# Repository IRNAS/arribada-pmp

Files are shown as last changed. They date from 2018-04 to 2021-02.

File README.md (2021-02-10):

# Arribada Penguin Monitoring Platform - v2 - development
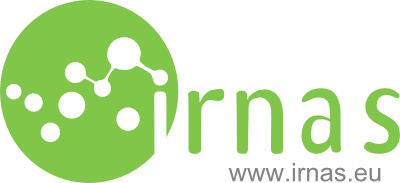
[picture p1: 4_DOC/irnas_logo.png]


Arribada Penguin Monitoring Platform (APMP) is a standalone device featuring a Raspberry Pi and a Raspberry Pi Camera Module with a number of additonal features. The below image is of previous version to form the list of necessary changes.



## Block diagram
Block diagram below shows the key features of Arribada PMP device. Device captures photos or video, measure temperature, humidity and air pressure, capture locations and charge batteries with solar cells. Penguin Monitoring Platform can communicates with LoRa and Rock Block or Lacuna.
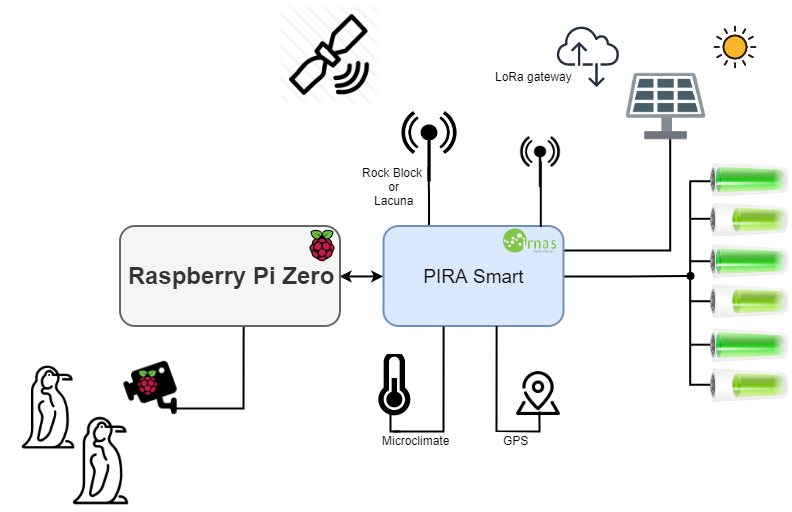
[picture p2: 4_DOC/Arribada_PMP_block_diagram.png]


## Key user features - v2
* Capture image/video at defined intervals
* Report system status/sensors via Lora (optional)
* Report system status/sensors via RockBlock Iridium (optional)
* Optional sensors:
  * Ultrasonic distance
  * Temperatures
  * GPS - location
* Power:
  * Batteries
  * Solar charging
* USB flash drive - user removable - contains all images and other captured data
  * contains images/videos
  * contains json with settings
* SD card with OS is read-only and not to be removed
* on/off switch
* 2x push button
  * button 1: test mode - push to turn on the system for 10 minutes
  * button 2: general purpose
* Test mode:
  * WiFi enabled, user can connect and check camera image or download all images
  * Each time test mode is enabled an image is taken.
* Bluetooth:
  * System status printout
  * Enable test mode
  * Configure settings
* Lora:
  * Enable test mode 
  * Configure settings
  * LacunaSpace communication
 
## Key user stories - v2
1. Penguin camera - Install on a pole in Antarctica. Arrive at location and turn on. Push button for test mode. See images via WiFi on smartphone or leave running and remove USB. To check camera alignment and correct operation. Leave device running for year or more, come pack and swap USB flash drive. Meanwhile real-time reporting via Lora or Lacuna, each day.
1. River camera - Install above a river with ultrasonic sensor and optional rockblock connection. Once above river enable the test mode via bluetooth. Check via WiFi the alignment and operation. Leave running and get real time sensor data. retrieve in a year to get back the photos.
1. TBD

## Configurable parameters - settings - v2
All the setings are defined as Environmental vairables in Linux, settings are changed using one of the following methods: json file present on the USB flash drive, system auto-updates values from it, via lora or via Balena if used

* User definable parameters:
 * capture schedule per month:
   * start time (UTC) - daily - fixed hour or `sunrise` (default 0:00)
   * end time (UTC) - daily - fixed hour or `sunset`(default 23:59)
   * interval (in minutes) - 0 to 24*60 (default 60)
 * location (automatic if GPS present):
   * lat (used for sunrise/sunset calculation)
   * lon (used for sunrise/sunset calculation)
 * capture type:
   * image
    * flash config
   * video
 * pira variables:
   * all timer values and defaults
   * lora parameters
   * rockblock parameters
   * sensor reporting interval
 * battery settings:
   * empty: default 10% - do not wake up the RPi below that
   * low-battery: default 30% - wake up only once a day
   * normal: general operation

## Specification

Device consists of:
 * Camera unit:
    * Raspberry Pi Zero W
    * Raspberry Pi Camera Module V2
    * Sandisk 16GB microSD card
    * Pira Smart V2 integrated board with battery mounts
    * 6x 18650 LiPo Cell 2900mAh/4.2V
    * Nanuk NANO 330 waterproof enclosure
    * I2C display for status
    * 2x user button
 * Optional:
    * Flash
    * Lora antenna
    * Rockblock Iridium or Lacuna module
    * Ultrasonic sensor
    * Thermometer
 * Solar power:
    * 2x Voltaic Systems 6V 6W solar panel
    * 2x Voltaic Systems solar panel extension cable
    * Multi-directional solar panel mount
 * Accessories
    * Allen-key tool for mounting
    * SD to microSD adapter
 * Mounting:
   * Simple strap mount (default)
   * Advanced KORUZA mount (optional)
 * Additionally required and not included
    * Pole (round or square) up to 50mm in diameter
    * Metric wrench size 13
    * Compass and tilt measuring device for pointing the solar panels
    
 ## Key desing considerations
 * Battery protection consider LC05111CMT for every 2 cells in parallel
 * Consider battery low temperature charge cutoor toprotect cells in winter

## License

All our projects are as usefully open-source as possible.

Hardware including documentation is licensed under [CERN OHL v.1.2. license](http://www.ohwr.org/licenses/cern-ohl/v1.2)

Firmware and software originating from the project is licensed under [GNU GENERAL PUBLIC LICENSE v3](http://www.gnu.org/licenses/gpl-3.0.en.html).

Open data generated by our projects is licensed under [CC0](https://creativecommons.org/publicdomain/zero/1.0/legalcode).

All our websites and additional documentation are licensed under [Creative Commons Attribution-ShareAlike 4 .0 Unported License](https://creativecommons.org/licenses/by-sa/4.0/legalcode).

What this means is that you can use hardware, firmware, software and documentation without paying a royalty and knowing that you'll be able to use your version forever. You are also free to make changes but if you share these changes then you have to do so on the same conditions that you enjoy.

Koruza, GoodEnoughCNC and IRNAS are all names and marks of Institut IRNAS Race. 
You may use these names and terms only to attribute the appropriate entity as required by the Open Licences referred to above. You may not use them in any other way and in particular you may not use them to imply endorsement or authorization of any hardware that you design, make or sell.

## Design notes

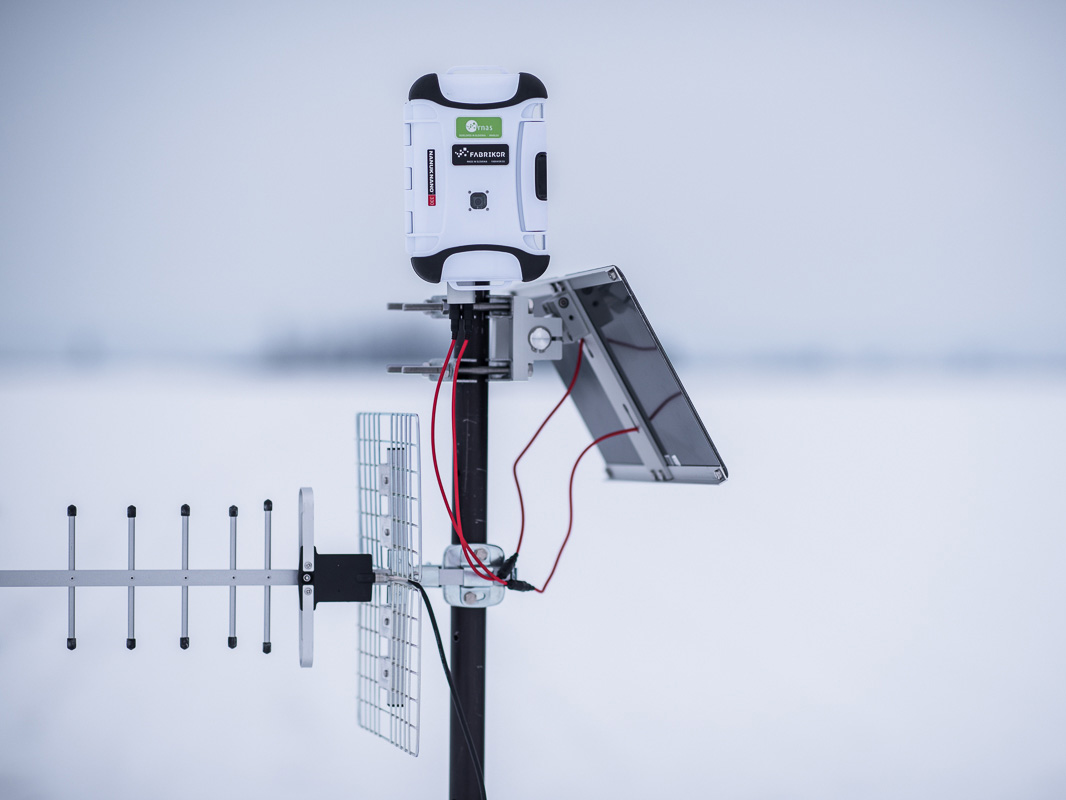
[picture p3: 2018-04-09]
pics/apmp-2.jpg

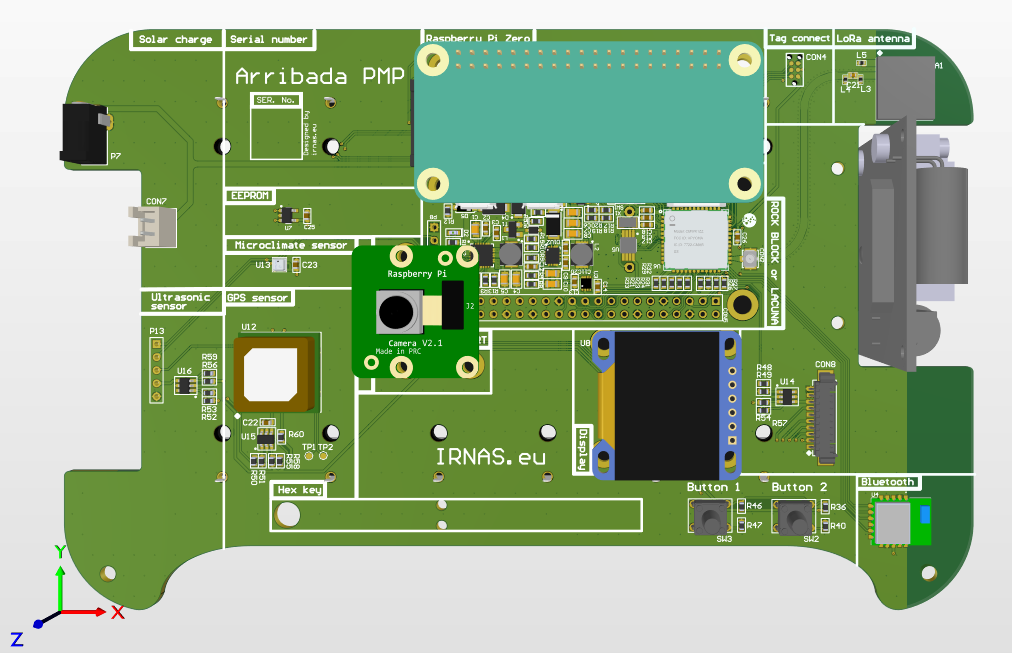
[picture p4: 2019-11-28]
6_RELEASE/V1.2/Arribada PMP_V1.2_SOURCE/04_OUTPUT_FILES/Pics/PMP_PCB_top.png

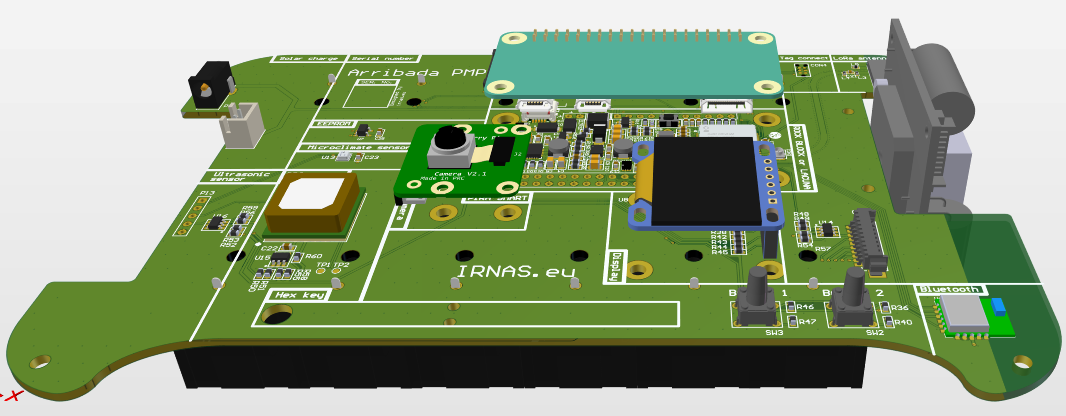
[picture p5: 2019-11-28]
6_RELEASE/V1.2/Arribada PMP_V1.2_SOURCE/04_OUTPUT_FILES/Pics/PMP_PCB_angle.png

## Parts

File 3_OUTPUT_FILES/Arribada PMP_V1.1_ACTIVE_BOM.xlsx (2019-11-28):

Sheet: Part List Report
 | Component list |  |  | Arribada PMP
 | Source Data From: | Arribada PMP_V0.1_ACTIVE_BOM.BomDoc |  |  | Contact:
 | Project: | Arribada-PMP.PrjPCB
 | Variant: | None |  |  |  |  |  |  | IRNAS
 | Report Date: | 30. 09. 2019 | 10:43 |  |  |  |  |  | www.irnas.eu
 | Print Date: | 2019-09-30 | 43738.447
# | Manufacturer Part Number 1 | Manufacturer 1 | Description | Footprint | Category | Quantity | Supplier 1 | Supplier Part Number 1 | Supplier Order Qty 1 | Supplier Stock 1 | Supplier Unit Price 1 | Supplier Subtotal 1 | Supplier Currency 1
1 |  |  |  | OLED SSD1306 |  | 1 |  | OLED SSD 1306 display
2 | C0603C106M8PACTU | KEMET | 10uf/0603/20% | CAP0603 |  | 2 | Farnell | 2820985 | 10 | 4806 | 0.32 | 3.19 | GBP
3 | SR42I010-R | Antenova | Antenna SMD -4dBi Gain 870MHz/928MHz Automotive 7-Pin SMD T/R | LORA_PCB_ANTENNA |  | 1 | Mouser | 237-SR42I010-R | 1 | 1418 | 2.36 | 2.36 | USD
4 |  |  | BATERRY HOLDER 18650 | BATTERY HOLDER 18650 |  | 6 |  | Battery holder for 18650
5 | CR-2032/VCN | Panasonic BSG | BATT LITH COIN 3V CELL PC PINS | CR-2032/VCN |  | 1 | Farnell | 1892670 | 1 | 1798 | 0.94 | 0.94 | GBP
6 |  |  | BATTERY PROTECTION | BATTERY PROTECTION |  | 3 |  | Battery protection
7 | CR0603-J/-000ELF | Bourns | BOURNS - CR0603-J/-000ELF - RES, THICK FILM, 0R, 5%, 0.1W, 0603 | RES0603 |  | 9 | Farnell | 2008343 | 10 | 35503 | 0.01 | 0.12 | GBP
8 | CR0603-J/-000ELF | Bourns | BOURNS - CR0603-J/-000ELF - RES, THICK FILM, 0R, 5%, 0.1W, 0603 | RES0603 |  | 10 | Farnell | 2008343 | 10 | 35503 | 0.01 | 0.12 | GBP
9 | HSMS-C190 | Broadcom | BROADCOM LIMITED - HSMS-C190 - LED, RED, 10MCD, 626NM | LED0603 |  | 1 | Farnell | 2497356
10 | U.FL-R-SMT-1(10) | Hirose | CONN UMC JACK STR 50 OHM SMD | ufl connector smd | Connectors, Interconnects | 1 | Farnell | 1688077
11 | LFXTAL009678 | IQD | CRYSTAL, 32.768KHZ, 12.5PF, SMD | LFXTAL009678 |  | 1 | Farnell | 2449398 | 5 | 4216 | 0.39 | 1.95 | GBP
12 | BZT52C6V2 | Diodes Zetex | DIODES INC. - BZT52C6V2 - DIODE, ZENER, 6.2V, 0.5W, SOD-123 | SOD123 |  | 1 | Farnell | 1902438 | 5 | 12142 | 0.12 | 0.62 | GBP
13 | DMG6602SVT | Diodes | DIODES INC. - DMG6602SVT - MOSFET, NP CH, , 30V, 3.4, ATSOT23 | TSOT26 |  | 1 | Farnell | 2061522 | 5 | 36143 | 0.29 | 1.48 | GBP
14 | DMG6602SVT | Diodes | Dual MOSFET, N and P Channel, 3.4 A, 30 V, 0.038 ohm, 10 V, 1 V | TSOT26 |  | 3 | Farnell | 2061522 | 5 | 36143 | 0.29 | 1.48 | GBP
15 |  |  | Header, 4-Pin | HDR1X4 |  | 2 |  | Header 2.54 mm, Header 2.54mm
16 |  |  | Header, 5-Pin | HDR1X5 |  | 1 |  | Header 2.54 mm
17 |  |  | Header, 11-Pin | HDR1X11 |  | 1 |  | Header 2.54mm
18 |  |  | Header, 20-Pin, Dual row | HDR2X20 |  | 2 |  | [NoParam], RPi header
19 | HSME-C191 | Broadcom Avago | HSME-C191 - LED, Green, SMD, 0603, 20 mA, 2.1 V, 572 nm | LED0603 |  | 1 | Farnell | 1219743 | 5 | 16346 | 0.31 | 1.53 | GBP
20 | BME280 | Bosch Tools | Humidity Temperature Sensor 0 ~ 100% RH I²C, SPI ±3% 1s Surface Mount | BME280 |  | 1 | Digi-Key | 828-1063-6-ND | 1 | 58503 | 6.55 | 6.55 | USD
21 | BQ24296RGET | Texas Instruments | IC LI+ CHARGER PWR MGMT 24VQFN | QFN4x4 | Integrated Circuits (ICs) | 1 | Farnell | 2373541
22 | MCP1810T-30I/J8A | Microchip | IC REG LINEAR 3V 150MA 8VDFN | VDFN_2x2 |  | 1 | Farnell | 2678433 | 1 | 1222 | 0.39 | 0.39 | GBP
23 | ISL1208IU8Z-T7A | Renesas | IC RTC/CALENDAR I2C LP 8MSOP | TSOP65P500X110-8N |  | 1 | Farnell | 2543322
24 | MCFT000028 | Multicomp | Inductor RF Chip Multi-Layer 4.3nH 0.3nH 100MHz 8Q-Factor Air 300mA 210mOhm DCR 0402 Paper T/R | IND0402 |  | 2 | Farnell | 1711735 | 10 | 13389 | 0.02 | 0.17 | GBP
25 | LQP02TQ4N2B02D | Murata | Inductor RF Chip Multi-Layer 4.3nH 0.3nH 100MHz 8Q-Factor Air 300mA 210mOhm DCR 0402 Paper T/R | IND0402 |  | 1 | Farnell | 2871406 | 10 | 19898 | 0.12 | 1.21 | GBP
26 | MINISMDC150F/24-2 | Littelfuse | LITTELFUSE - MINISMDC150F/24-2 - POLYSWITCH, SMD, 1812, 1.5A | Chip2PinSM127P600-8N |  | 1 | Farnell | 1345929
27 | CMWX1ZZABZ-091 | Murata | Lora Module Murata | Lora Module ES0 |  | 1 | Farnell | 2802546 | 1 | 105 | 15.15 | 15.15 | GBP
28 | 24AA02E48T-I/OT | Microchip | MICROCHIP 24AA02E48T-I/OT EEPROM, EUI-48 Node Identity, 2 Kbit, 2 BLK (128K x 8bit), 400 kHz, I2C, SOT-23, 5 Pins | SOT95P280X145-5N |  | 1 | Farnell | 1688855 | 1 | 16808 | 0.18 | 0.18 | GBP
29 | RN4871-V/RM118 | Microchip | MICROCHIP RN4871-V/RM118 BLE MOD W/ANTENNA, 2.442MHZ, 0.1DBI New | RN4871 |  | 1 | Farnell | 2664514 | 1 | 2422 | 5.71 | 5.71 | GBP
30 | MCWR06X1000FTL | Multicomp | MULTICOMP - MC0063W06031100R - RES, THICK FILM, 100R, 1%, 0.063W, 0603 | RES0603 |  | 2 | Farnell | 2447227 | 10 | 462054 | 0.01 | 0.06 | EUR
31 | MC0.063W06031%100R | Multicomp | MULTICOMP - MC0063W06031100R - RES, THICK FILM, 100R, 1%, 0.063W, 0603 | RES0603 |  | 9 | Farnell | 9330364
32 | MC0603B473K500CT | Multicomp | MULTICOMP - MC0603B473K500CT - CAP, MLCC, X7R, 47NF, 50V, 0603 | CAP0603 |  | 1 | Farnell | 1759116 | 10 | 36181 | 0.02 | 0.22 | GBP
33 | MC0805X226M6R3CT | Multicomp | MULTICOMP - MC0805X226M6R3CT - CAP, MLCC, X5R, 22UF, 0805 | CAP0805 |  | 4 | Farnell | 1759415
34 | MCMR06X102JTL | Multicomp | MULTICOMP - MCMR06X102 JTL - RES, CERAMIC, 1K, 5%, 0.1W, 0603 | RES0603 |  | 2 | Farnell | 2073354 | 10 | 150 | 0.01 | 0.07 | GBP
35 | MCMR06X103JTL | Multicomp | MULTICOMP - MCMR06X103 JTL - RES, CERAMIC, 10K, 5%, 0.1W, 0603 | RES0603 |  | 3 | Farnell | 2073356 | 10 | 8524 | 0.01 | 0.08 | GBP
36 | MCMR06X103JTL | Multicomp | MULTICOMP - MCMR06X103 JTL - RES, CERAMIC, 10K, 5%, 0.1W, 0603 | RES0603 |  | 3 | Farnell | 2073356 | 10 | 8524 | 0.01 | 0.08 | GBP
37 | MCMR06X104JTL | Multicomp | MULTICOMP - MCMR06X104 JTL - RES, CERAMIC, 100K, 5%, 0.1W, 0603 | RES0603 |  | 4 | Farnell | 2073357 | 10 | 19720 | 0.01 | 0.07 | GBP
38 | MCMR06X104JTL | Multicomp | MULTICOMP - MCMR06X104 JTL - RES, CERAMIC, 100K, 5%, 0.1W, 0603 | RES0603 |  | 6 | Farnell | 2073357 | 10 | 19720 | 0.01 | 0.07 | GBP
39 | MCMR06X471JTL | Multicomp | MULTICOMP - MCMR06X471 JTL - RES, CERAMIC, 470R, 5%, 0.1W, 0603 | RES0603 |  | 2 | Farnell | 2073513 | 10 | 7623 | 0.01 | 0.05 | GBP
40 | MCMR06X2201FTL | Multicomp | MULTICOMP - MCMR06X2201FTL - RES, CERAMIC, 2K2, 1%, 0.1W, 0603 | RES0603 |  | 1 | Farnell | 2073429 | 10 | 25875 | 0.01 | 0.10 | GBP
41 | MCMR06X4701FTL | Multicomp | MULTICOMP - MCMR06X4701FTL - RES, CERAMIC, 4K7, 1%, 0.1W, 0603 | RES0603 |  | 2 | Farnell | 2073509 | 10 | 27235 | 0.01 | 0.10 | GBP
42 | MCMR06X5601FTL | Multicomp | MULTICOMP - MCMR06X5601FTL - RES, CERAMIC, 5K6, 1%, 0.1W, 0603 | RES0603 |  | 1 | Farnell | 2073537 | 10 | 960 | 0.01 | 0.10 | GBP
43 | MCWR06X1503FTL | Multicomp | MULTICOMP - MCWR06X1503FTL - RES, THICK FILM, 150KOHM, 1%, 0.1W | RES0603 |  | 1 | Farnell | 2447254 | 10 | 63490 | 0.01 | 0.05 | GBP
44 | MCWR06X2200FTL | Multicomp | MULTICOMP - MCWR06X2200FTL - RES, THICK FILM, 220R, 1%, 0.1W, 0603 | RES0603 |  | 1 | Farnell | 2447298 | 10 | 268348 | 0.01 | 0.06 | EUR
45 | MCWR06X3302FTL | Multicomp | MULTICOMP - MCWR06X3302FTL - RES, THICK FILM, 33K, 1%, 0.1W, 0603 | RES0603 |  | 1 | Farnell | 2447342 | 10 | 85218 | 0.01 | 0.05 | GBP
46 | MCWR06X3901FTL | Multicomp | MULTICOMP - MCWR06X3901FTL - RES, THICK FILM, 3K9, 1%, 0.1W, 0603 | RES0603 |  | 1 | Farnell | 2447363 | 10 | 27101 | 0.01 | 0.05 | GBP
47 | C0402C229C5GACTU | KEMET | Multilayer Ceramic Capacitors MLCC - SMD/SMT 50volts 1.8pF C0G | CAP0402 |  | 1 | Farnell | 1800795 | 10 | 31735 | 0.05 | 0.53 | GBP
48 | GRM188R61C106KAALD | Murata | Multilayer Ceramic Capacitors MLCC - SMD/SMT 0603 10uF 16volts X5R 10% | CAP0603 |  | 2 | Farnell | 2611923 | 10 | 94340 | 0.26 | 2.61 | GBP
49 | FDSD0420-H-1R5M=P3 | Murata | MURATA - FDSD0420-H-1R5M=P3 - INDUCTOR, SHIELDED, 1.5UH, 5.1A, 20% | FDSD0402 |  | 2 | Farnell | 2530091 | 5 | 15 | 0.83 | 4.17 | GBP
50 | GRM188R61C475KAAJD | Murata | MURATA - GRM188R61C475KAAJD - CAP, MLCC, X5R, 4.7UF, 16V, 0603 | CAP0603 |  | 1 | Farnell | 2611924 | 10 | 81661 | 0.24 | 2.39 | GBP
51 | GRM188R61C475KAAJD | Murata | MURATA - GRM188R61C475KAAJD - CAP, MLCC, X5R, 4.7UF, 16V, 0603 | CAP0603 |  | 1 | Farnell | 2611924 | 10 | 81661 | 0.24 | 2.39 | GBP
52 | GRM188R61H105KAALD | Murata | MURATA - GRM188R61H105KAALD - CAP, MLCC, X5R, 1UF, 50V, 0603 | CAP0603 |  | 2 | Farnell | 1845736
53 | GRM188R61H105KAALD | Murata | MURATA - GRM188R61H105KAALD - CAP, MLCC, X5R, 1UF, 50V, 0603 | CAP0603 |  | 1 | Farnell | 1845736
54 | GRM188R71C104KA01J | Murata | MURATA - GRM188R71C104KA01J - CAP, MLCC, X7R, 0.1UF, 16V, 0603 | CAP0603 |  | 4 | Farnell | 2688519
55 | GRM188R71C104KA01J | Murata | MURATA - GRM188R71C104KA01J - CAP, MLCC, X7R, 0.1UF, 16V, 0603 | CAP0603 |  | 2 | Farnell | 2688519
56 | MM3Z3V0T1G | ON Semiconductor | ON SEMICONDUCTOR - MM3Z3V0T1G - ZENER DIODE, 200MW, 3V, SOD-323 | SOD-323 2L |  | 1 | Farnell | 2463510 | 5 | 21905 | 0.12 | 0.61 | GBP
57 | MMBT3904 | NXP Semiconductors | ON SEMICONDUCTOR/FAIRCHILD - MMBT3904 - TRANSISTOR, NPN, SOT-23 | SOT23127P600-8N |  | 1 | Farnell | 9846727 | 5 | 72000 | 0.14 | 0.68 | GBP
58 |  |  | PCB top overlay Serial number frame | SERIAL NUMBER |  | 1
59 | 694102303002 | Wurth Electronics | Power Barrel Connector Jack 1.05mm ID (0.041"), 3.50mm OD (0.138") Through Hole, Right Angle | 732-5922-ND |  | 1 | Farnell | 2472141 | 10 | 183 | 0.63 | 6.30 | GBP
60 | SAM-M8Q-0 | u-blox | SAM-M8 RF Receiver BeiDou, Galileo, GLONASS, GNSS, GPS -160dBm | SAM-M8Q |  | 1 | Digi-Key | 672-1054-1-ND | 1 | 4378 | 25.00 | 25.00 | USD
61 | 1PS76SB10,115 | Nexperia | Small Signal Schottky Diode, Single, 30 V, 200 mA, 320 mV, 800 mA, 125 °C | SOD-323 |  | 2 | Farnell | 1081179 | 5 | 124792 | 0.17 | 0.85 | GBP
62 | MC0603X225K6R3CT | Multicomp | SMD Multilayer Ceramic Capacitor, 2.2 µF, 6.3 V, 0603 [1608 Metric], ± 10%, X5R, MC Series | CAP0603 |  | 1 | Farnell | 1759392 | 10 | 15721 | 0.06 | 0.55 | GBP
63 |  |  | SWITCH TACTILE SPST-NO 0.05A 32V | Tactile button |  | 1 | C&K Components | 2845727
64 | B3F-1070 | Omron | Tactile Switch, B3F Series, Top Actuated, Through Hole, Round Button, 100 gf, 50mA at 24VDC | BTN B3F-1070 |  | 2 | Farnell | 959698 | 5 | 3258 | 0.25 | 1.26 | GBP
65 | MC0805X106K160CT | Multicomp | TDK - CGA4J1X5R1C106K125AC - CAP, MLCC, X5R, 10UF, 16V, 0805 | CAP0805 |  | 4 | Farnell | 2320856
66 |  |  | TEST POINT ROUND SMD | TestPoint:1.2x1.2mm |  | 2
67 | TPS630701RNMT | Texas Instruments | TEXAS INSTRUMENTS - TPS630701RNMT - DC/DC CONV, BUCK-BOOST, 2.4MHZ, VQFN-15 | VQFN TPS |  | 1 | Farnell | 2643432
68 | B57321V2103J060 | TDK EPCOS | Thermistor, NTC, 10 kohm, B57321V2 Series, 4000 K, SMD, 0603 [1608 Metric] | RES0603 |  | 1 | Farnell | 1299914 | 10 | 24794 | 0.19 | 1.87 | GBP
69 | CRCW0603226KFKEA | Vishay | Thick Film Resistors - SMD 1/10watt 226Kohms 1% | RES0603 |  | 1 | Farnell | 2138531
70 | RCA060310R0FKEA | Vishay Dale | VISHAY - RCA060310R0FKEA - RES, AUTO, THICK FILM, 10R, 1%, 0603 | RES0603 |  | 1 | Farnell | 2616585 | 10 | 6813 | 0.01 | 0.12 | GBP
71 | RS1J-E3/61T | Vishay Semiconductors | VISHAY - RS1J-E3/61T.. - DIODE, FAST, 1A, 600V, SMD | SMC/DO-214AC |  | 1 | Farnell | 9550143 | 5 | 4450 | 0.25 | 1.24 | GBP
72 | SE30AFG-M3/6A | Vishay Semiconductors | VISHAY - SE30AFG-M3/6A - RECTIFIER, ESD, 400V, 3A, DO-221AC | SODFL127P600-8N |  | 2 | Farnell | 2313878 | 5 | 22049 | 0.31 | 1.57 | GBP
73 | 53261-1071 | Molex | Wire-To-Board Connector, Right Angle, 1.25 mm, 10 Contacts, Header, PicoBlade 53261 Series | PICOBLADE 10PIN |  | 1 | Farnell | 1125377 | 1 | 4313 | 0.86 | 0.86 | GBP
74 | B2B-XH-A(LF)(SN) | JST | Wire-To-Board Connector, Vertical, 2.5 mm, 2 Contacts, Header, XH Series, Through Hole, 1 Rows | JST_2PIN_TH |  | 1 | Farnell | 1516276 | 100 | 185326 | 0.06 | 6.06 | GBP
 |  |  |  |  |  | 145 |  |  | 449 |  |  | 103.444
Approved |  |  |  | Notes
 |  |  |  | pcs: |  | 1 |  | Total |  | 103.444 |  | USD
 |  |  |  |  |  |  |  | Price for 1pcs |  | 103.44 |  | USD

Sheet: Project Information
Project Full Path | D:\OneDrive\IRNAS-Common\_NEW-IRNAS-COMMON\Arribada-PMP\Electronics\Arribada-PMP.PrjPCB
Project Filename | Arribada-PMP.PrjPCB
Variant Name | None
Data-Source Filename | Arribada PMP_V0.1_ACTIVE_BOM.BomDoc
Data-Source Full Path | D:\OneDrive\IRNAS-Common\_NEW-IRNAS-COMMON\Arribada-PMP\Electronics\04_OUTPUT_FILES\Arribada PMP_V0.1_ACTIVE_BOM.BomDoc
Title | ACTIVE_BOM for BOM Document [Arribada PMP_V0.1_ACTIVE_BOM.BomDoc]
Total Quantity | 145
Report Time | 10:43
Report Date | 30. 09. 2019
Report Date & Tine | 30. 09. 2019 10:43
Output Name | ACTIVE_BOM
Output Type | BOM_PartType
Output Generator Name | BOM
Output Generator Description | Bill of Materials

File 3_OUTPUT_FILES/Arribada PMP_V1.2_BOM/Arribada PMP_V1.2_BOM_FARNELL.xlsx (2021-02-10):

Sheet: Altium Output
Supplier Part Number 1 | Quantity | Description | Designator | Supplier 1 | IRNAS Part No. | No PCB | Projekt | Farnell
237-SR42I010-R | 1 | Antenna SMD -4dBi Gain 870MHz/928MHz Automotive 7-Pin SMD T/R | A1 | Mouser |  | 5 |  | 237-SR42I010-R, 5,
2320856 | 4 | TDK - CGA4J1X5R1C106K125AC - CAP, MLCC, X5R, 10UF, 16V, 0805 | C1, C4, C5, C6 | Farnell |  | 5 |  | 2320856, 20,
2611924 | 2 | MURATA - GRM188R61C475KAAJD - CAP, MLCC, X5R, 4.7UF, 16V, 0603 | C2, C13 | Farnell | [NoParam], I-200001 | 5 |  | 2611924, 10,
1759116 | 1 | MULTICOMP - MC0603B473K500CT - CAP, MLCC, X7R, 47NF, 50V, 0603 | C3 | Farnell |  | 5 |  | 1759116, 5,
1759415 | 4 | MULTICOMP - MC0805X226M6R3CT - CAP, MLCC, X5R, 22UF, 0805 | C7, C8, C9, C10 | Farnell |  | 5 |  | 1759415, 20,
2611923 | 2 | Multilayer Ceramic Capacitors MLCC - SMD/SMT 0603 10uF 16volts X5R 10% | C11, C20 | Farnell |  | 5 |  | 2611923, 10,
2688519 | 7 | MURATA - GRM188R71C104KA01J - CAP, MLCC, X7R, 0.1UF, 16V, 0603 | C12, C15, C18, C22, C23, C25, C28 | Farnell | [NoParam], I-200005 | 5 |  | 2688519, 35,
1759392 | 1 | SMD Multilayer Ceramic Capacitor, 2.2 µF, 6.3 V, 0603 [1608 Metric], ± 10%, X5R, MC Series | C14 | Farnell |  | 5 |  | 1759392, 5,
1845736 | 6 | MURATA - GRM188R61H105KAALD - CAP, MLCC, X5R, 1UF, 50V, 0603 | C16, C17, C24, C26, C27, C29 | Farnell | I-200006, [NoParam] | 5 |  | 1845736, 30,
2820985 | 1 | 10uf/0603/20% | C19 | Farnell |  | 5 |  | 2820985, 5,
2627398 | 1 | Multilayer Ceramic Capacitors MLCC - SMD/SMT 50volts 1.8pF C0G | C21 | Farnell | / | 5 |  | 2627398, 5,
1688077 | 1 | CONN UMC JACK STR 50 OHM SMD | CON2 | Farnell |  | 5 |  | 1688077, 5,
1892670 | 1 | BATT LITH COIN 3V CELL PC PINS | CON3 | Farnell |  | 5 |  | 1892670, 5,
 | 7 | Header, 20-Pin, Dual row, TEST POINT ROUND SMD | CON5, TP1, TP2, TP3, TP4, TP5, TP6 |  |  | 5 |  | , 35,
RPi header | 1 | Header, 20-Pin, Dual row | CON6 |  |  | 5 |  | RPi header, 5,
1516276 | 1 | Wire-To-Board Connector, Vertical, 2.5 mm, 2 Contacts, Header, XH Series, Through Hole, 1 Rows | CON7 | Farnell |  | 5 |  | 1516276, 5,
1125377 | 1 | Wire-To-Board Connector, Right Angle, 1.25 mm, 10 Contacts, Header, PicoBlade 53261 Series | CON8 | Farnell |  | 5 |  | 1125377, 5,
9550143 | 1 | VISHAY - RS1J-E3/61T.. - DIODE, FAST, 1A, 600V, SMD | D1 | Farnell |  | 5 |  | 9550143, 5,
2497356 | 1 | BROADCOM LIMITED - HSMS-C190 - LED, RED, 10MCD, 626NM | D2 | Farnell |  | 5 |  | 2497356, 5,
2313878 | 2 | VISHAY - SE30AFG-M3/6A - RECTIFIER, ESD, 400V, 3A, DO-221AC | D3, D4 | Farnell |  | 5 |  | 2313878, 10,
1902438 | 1 | DIODES INC. - BZT52C6V2 - DIODE, ZENER, 6.2V, 0.5W, SOD-123 | D5 | Farnell |  | 5 |  | 1902438, 5,
2463510 | 1 | ON SEMICONDUCTOR - MM3Z3V0T1G - ZENER DIODE, 200MW, 3V, SOD-323 | D6 | Farnell |  | 5 |  | 2463510, 5,
1219743 | 1 | HSME-C191 - LED, Green, SMD, 0603, 20 mA, 2.1 V, 572 nm | D7 | Farnell |  | 5 |  | 1219743, 5,
1345929 | 1 | LITTELFUSE - MINISMDC150F/24-2 - POLYSWITCH, SMD, 1812, 1.5A | F1 | Farnell |  | 5 |  | 1345929, 5,
2530091 | 2 | MURATA - FDSD0420-H-1R5M=P3 - INDUCTOR, SHIELDED, 1.5UH, 5.1A, 20% | L1, L2 | Farnell |  | 5 |  | 2530091, 10,
1343066 | 1 | Inductor RF Chip Multi-Layer 4.3nH 0.3nH 100MHz 8Q-Factor Air 300mA 210mOhm DCR 0402 Paper T/R | L5 | Farnell | / | 5 |  | 1343066, 5,
Header 2.54mm | 2 | Header, 11-Pin, Header, 4-Pin | P2, P8 |  |  | 5 |  | Header 2.54mm, 10,
Header 2.54 mm | 1 | Header, 4-Pin | P4 |  |  | 5 |  | Header 2.54 mm, 5,
Battery holder for 18650 | 6 | BATERRY HOLDER 18650 | P5, P6, P9, P10, P11, P12 |  |  | 5 |  | Battery holder for 18650, 30,
2472141 | 1 | Power Barrel Connector Jack 1.05mm ID (0.041"), 3.50mm OD (0.138") Through Hole, Right Angle | P7 | Farnell |  | 5 |  | 2472141, 5,
2073513 | 2 | MULTICOMP - MCMR06X471 JTL - RES, CERAMIC, 470R, 5%, 0.1W, 0603 | R1, R14 | Farnell |  | 5 |  | 2073513, 10,
1299914 | 1 | Thermistor, NTC, 10 kohm, B57321V2 Series, 4000 K, SMD, 0603 [1608 Metric] | R2 | Farnell |  | 5 |  | 1299914, 5,
2073537 | 1 | MULTICOMP - MCMR06X5601FTL - RES, CERAMIC, 5K6, 1%, 0.1W, 0603 | R3 | Farnell |  | 5 |  | 2073537, 5,
2008343 | 19 | BOURNS - CR0603-J/-000ELF - RES, THICK FILM, 0R, 5%, 0.1W, 0603 | R4, R17, R18, R19, R20, R21, R22, R23, R24, R26, R27, R31, R33, R37, R41, R43, R45, R63, R66 | Farnell | [NoParam], I-100011 | 5 |  | 2008343, 95,
2447363 | 1 | MULTICOMP - MCWR06X3901FTL - RES, THICK FILM, 3K9, 1%, 0.1W, 0603 | R5 | Farnell |  | 5 |  | 2447363, 5,
2073509 | 2 | MULTICOMP - MCMR06X4701FTL - RES, CERAMIC, 4K7, 1%, 0.1W, 0603 | R6, R11 | Farnell | I-100003 | 5 |  | 2073509, 10,
2447298 | 1 | MULTICOMP - MCWR06X2200FTL - RES, THICK FILM, 220R, 1%, 0.1W, 0603 | R7 | Farnell |  | 5 |  | 2447298, 5,
2447254 | 1 | MULTICOMP - MCWR06X1503FTL - RES, THICK FILM, 150KOHM, 1%, 0.1W | R8 | Farnell |  | 5 |  | 2447254, 5,
2073356 | 6 | MULTICOMP - MCMR06X103 JTL - RES, CERAMIC, 10K, 5%, 0.1W, 0603 | R9, R10, R15, R36, R46, R59 | Farnell | [NoParam], I-100008 | 5 |  | 2073356, 30,
2616585 | 1 | VISHAY - RCA060310R0FKEA - RES, AUTO, THICK FILM, 10R, 1%, 0603 | R12 | Farnell |  | 5 |  | 2616585, 5,
2447342 | 1 | MULTICOMP - MCWR06X3302FTL - RES, THICK FILM, 33K, 1%, 0.1W, 0603 | R13 | Farnell |  | 5 |  | 2447342, 5,
2073354 | 2 | MULTICOMP - MCMR06X102 JTL - RES, CERAMIC, 1K, 5%, 0.1W, 0603 | R16, R47 | Farnell | I-100042 | 5 |  | 2073354, 10,
9330364 | 10 | MULTICOMP - MC0063W06031100R - RES, THICK FILM, 100R, 1%, 0.063W, 0603 | R25, R28, R30, R48, R50, R56, R57, R58, R60, R62 | Farnell | I-100009 | 5 |  | 9330364, 50,
2138531 | 1 | Thick Film Resistors - SMD 1/10watt 226Kohms 1% | R29 | Farnell |  | 5 |  | 2138531, 5,
2073357 | 7 | MULTICOMP - MCMR06X104 JTL - RES, CERAMIC, 100K, 5%, 0.1W, 0603 | R32, R49, R51, R52, R53, R54, R55 | Farnell | [NoParam], I-100007 | 5 |  | 2073357, 35,
2073429 | 1 | MULTICOMP - MCMR06X2201FTL - RES, CERAMIC, 2K2, 1%, 0.1W, 0603 | R40 | Farnell | I-100024 | 5 |  | 2073429, 5,
2845727 | 2 | SWITCH TACTILE SPST-NO 0.05A 32V | S1, SW1 | Farnell, C&K Components |  | 5 |  | 2845727, 10,
959698 | 2 | Tactile Switch, B3F Series, Top Actuated, Through Hole, Round Button, 100 gf, 50mA at 24VDC | SW2, SW3 | Farnell |  | 5 |  | 959698, 10,
9846727 | 1 | ON SEMICONDUCTOR/FAIRCHILD - MMBT3904 - TRANSISTOR, NPN, SOT-23 | T1 | Farnell |  | 5 |  | 9846727, 5,
2373541 | 1 | IC LI+ CHARGER PWR MGMT 24VQFN | U1 | Farnell |  | 5 |  | 2373541, 5,
2643432 | 1 | TEXAS INSTRUMENTS - TPS630701RNMT - DC/DC CONV, BUCK-BOOST, 2.4MHZ, VQFN-15 | U2 | Farnell |  | 5 |  | 2643432, 5,
2678433 | 1 | IC REG LINEAR 3V 150MA 8VDFN | U3 | Farnell |  | 5 |  | 2678433, 5,
2061522 | 3 | Dual MOSFET, N and P Channel, 3.4 A, 30 V, 0.038 ohm, 10 V, 1 V | U4, U14, U15 | Farnell |  | 5 |  | 2061522, 15,
2543322 | 1 | IC RTC/CALENDAR I2C LP 8MSOP | U5 | Farnell |  | 5 |  | 2543322, 5,
2802546 | 1 | Lora Module Murata | U6 | Farnell |  | 5 |  | 2802546, 5,
1688855 | 1 | MICROCHIP 24AA02E48T-I/OT EEPROM, EUI-48 Node Identity, 2 Kbit, 2 BLK (128K x 8bit), 400 kHz, I2C, SOT-23, 5 Pins | U7 | Farnell |  | 5 |  | 1688855, 5,
OLED SSD 1306 display | 1 |  | U8 |  |  | 5 |  | OLED SSD 1306 display, 5,
Battery protection | 3 | BATTERY PROTECTION | U9, U10, U11 |  |  | 5 |  | Battery protection, 15,
672-1054-1-ND | 1 | SAM-M8 RF Receiver BeiDou, Galileo, GLONASS, GNSS, GPS -160dBm | U12 | Digi-Key |  | 5 |  | 672-1054-1-ND, 5,
828-1063-6-ND | 1 | Humidity Temperature Sensor 0 ~ 100% RH I²C, SPI ±3% 1s Surface Mount | U13 | Digi-Key |  | 5 |  | 828-1063-6-ND, 5,
3118263 | 1 | Analogue Switch, 2 Channels, SPDT, 0.34 ohm, 1.65V to 3.6V, VSSOP, 10 Pins | U16 | Farnell |  | 5 |  | 3118263, 5,
2449398 | 1 | CRYSTAL, 32.768KHZ, 12.5PF, SMD | X1 | Farnell |  | 5 |  | 2449398, 5,
 |  |  |  |  |  | 5 |  | , 0,
 |  |  |  |  |  | 5 |  | , 0,
 |  |  |  |  |  | 5 |  | , 0,
 |  |  |  |  |  | 5 |  | , 0,
 |  |  |  |  |  | 5 |  | , 0,
 |  |  |  |  |  | 5 |  | , 0,
 |  |  |  |  |  | 5 |  | , 0,
 |  |  |  |  |  | 5 |  | , 0,
 |  |  |  |  |  | 5 |  | , 0,
 |  |  |  |  |  | 5 |  | , 0,
 |  |  |  |  |  | 5 |  | , 0,
 |  |  |  |  |  | 5 |  | , 0,
 |  |  |  |  |  | 5 |  | , 0,
 |  |  |  |  |  | 5 |  | , 0,
 |  |  |  |  |  | 5 |  | , 0,
 |  |  |  |  |  | 5 |  | , 0,
 |  |  |  |  |  | 5 |  | , 0,
 |  |  |  |  |  | 5 |  | , 0,
 |  |  |  |  |  | 5 |  | , 0,
 |  |  |  |  |  | 5 |  | , 0,
 |  |  |  |  |  | 5 |  | , 0,
 |  |  |  |  |  | 5 |  | , 0,
 |  |  |  |  |  | 5 |  | , 0,
 |  |  |  |  |  | 5 |  | , 0,
 |  |  |  |  |  | 5 |  | , 0,
 |  |  |  |  |  | 5 |  | , 0,
 |  |  |  |  |  | 5 |  | , 0,
 |  |  |  |  |  | 5 |  | , 0,
 |  |  |  |  |  | 5 |  | , 0,
 |  |  |  |  |  | 5 |  | , 0,
 |  |  |  |  |  | 5 |  | , 0,
 |  |  |  |  |  | 5 |  | , 0,
 |  |  |  |  |  | 5 |  | , 0,
 |  |  |  |  |  | 5 |  | , 0,
 |  |  |  |  |  | 5 |  | , 0,
 |  |  |  |  |  | 5 |  | , 0,
 |  |  |  |  |  | 5 |  | , 0,
 |  |  |  |  |  | 5 |  | , 0,
 |  |  |  |  |  | 5 |  | , 0,
 |  |  |  |  |  | 5 |  | , 0,
 |  |  |  |  |  | 5 |  | , 0,
 |  |  |  |  |  | 5 |  | , 0,
 |  |  |  |  |  | 5 |  | , 0,
 |  |  |  |  |  | 5 |  | , 0,
 |  |  |  |  |  | 5 |  | , 0,
 |  |  |  |  |  | 5 |  | , 0,
 |  |  |  |  |  | 5 |  | , 0,
 |  |  |  |  |  | 5 |  | , 0,
 |  |  |  |  |  | 5 |  | , 0,
 |  |  |  |  |  | 5 |  | , 0,
 |  |  |  |  |  | 5 |  | , 0,
 |  |  |  |  |  | 5 |  | , 0,
 |  |  |  |  |  | 5 |  | , 0,
 |  |  |  |  |  | 5 |  | , 0,
 |  |  |  |  |  | 5 |  | , 0,
 |  |  |  |  |  | 5 |  | , 0,
 |  |  |  |  |  | 5 |  | , 0,
 |  |  |  |  |  | 5 |  | , 0,
 |  |  |  |  |  | 5 |  | , 0,
 |  |  |  |  |  | 5 |  | , 0,
 |  |  |  |  |  | 5 |  | , 0,
 |  |  |  |  |  | 5 |  | , 0,
 |  |  |  |  |  | 5 |  | , 0,
 |  |  |  |  |  | 5 |  | , 0,
 |  |  |  |  |  | 5 |  | , 0,
 |  |  |  |  |  | 5 |  | , 0,
 |  |  |  |  |  | 5 |  | , 0,
 |  |  |  |  |  | 5 |  | , 0,
 |  |  |  |  |  | 5 |  | , 0,
 |  |  |  |  |  | 5 |  | , 0,
 |  |  |  |  |  | 5 |  | , 0,
 |  |  |  |  |  | 5 |  | , 0,
 |  |  |  |  |  | 5 |  | , 0,
 |  |  |  |  |  | 5 |  | , 0,
 |  |  |  |  |  | 5 |  | , 0,
 |  |  |  |  |  | 5 |  | , 0,
 |  |  |  |  |  | 5 |  | , 0,
 |  |  |  |  |  | 5 |  | , 0,
 |  |  |  |  |  | 5 |  | , 0,
 |  |  |  |  |  | 5 |  | , 0,
 |  |  |  |  |  | 5 |  | , 0,
 |  |  |  |  |  | 5 |  | , 0,
 |  |  |  |  |  | 5 |  | , 0,
 |  |  |  |  |  | 5 |  | , 0,
 |  |  |  |  |  | 5 |  | , 0,
 |  |  |  |  |  | 5 |  | , 0,
 |  |  |  |  |  | 5 |  | , 0,
 |  |  |  |  |  | 5 |  | , 0,
 |  |  |  |  |  | 5 |  | , 0,
 |  |  |  |  |  | 5 |  | , 0,
 |  |  |  |  |  | 5 |  | , 0,
 |  |  |  |  |  | 5 |  | , 0,
 |  |  |  |  |  | 5 |  | , 0,
 |  |  |  |  |  | 5 |  | , 0,
 |  |  |  |  |  | 5 |  | , 0,

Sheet: Farnell Order
Supplier Part Number 1 | Quantity | Description | Designator | No. PCBs | Material in stock
237-SR42I010-R | 0 | Antenna SMD -4dBi Gain 870MHz/928MHz Automotive 7-Pin SMD T/R | A1
2320856 | 0 | TDK - CGA4J1X5R1C106K125AC - CAP, MLCC, X5R, 10UF, 16V, 0805 | C1, C4, C5, C6
2449398 | 0 | CRYSTAL, 32.768KHZ, 12.5PF, SMD | X1
0 | 0 | 0 | 0
0 | 0 | 0 | 0
0 | 0 | 0 | 0
0 | 0 | 0 | 0
0 | 0 | 0 | 0
0 | 0 | 0 | 0
0 | 0 | 0 | 0
0 | 0 | 0 | 0
0 | 0 | 0 | 0
0 | 0 | 0 | 0
0 | 0 | 0 | 0
0 | 0 | 0 | 0
0 | 0 | 0 | 0
0 | 0 | 0 | 0
0 | 0 | 0 | 0
0 | 0 | 0 | 0
0 | 0 | 0 | 0
0 | 0 | 0 | 0
0 | 0 | 0 | 0
0 | 0 | 0 | 0
0 | 0 | 0 | 0
0 | 0 | 0 | 0
0 | 0 | 0 | 0
0 | 0 | 0 | 0
0 | 0 | 0 | 0
0 | 0 | 0 | 0
0 | 0 | 0 | 0
0 | 0 | 0 | 0
0 | 0 | 0 | 0
0 | 0 | 0 | 0
0 | 0 | 0 | 0
0 | 0 | 0 | 0
0 | 0 | 0 | 0
0 | 0 | 0 | 0
0 | 0 | 0 | 0
0 | 0 | 0 | 0
0 | 0 | 0 | 0
0 | 0 | 0 | 0
0 | 0 | 0 | 0
0 | 0 | 0 | 0
0 | 0 | 0 | 0
0 | 0 | 0 | 0
0 | 0 | 0 | 0
0 | 0 | 0 | 0
0 | 0 | 0 | 0
0 | 0 | 0 | 0
0 | 0 | 0 | 0
0 | 0 | 0 | 0
0 | 0 | 0 | 0
0 | 0 | 0 | 0
0 | 0 | 0 | 0
0 | 0 | 0 | 0
0 | 0 | 0 | 0
0 | 0 | 0 | 0
0 | 0 | 0 | 0
0 | 0 | 0 | 0
0 | 0 | 0 | 0
0 | 0 | 0 | 0
0 | 0 | 0 | 0
0 | 0 | 0 | 0
0 | 0 | 0 | 0
0 | 0 | 0 | 0
0 | 0 | 0 | 0
0 | 0 | 0 | 0
0 | 0 | 0 | 0
0 | 0 | 0 | 0
0 | 0 | 0 | 0
0 | 0 | 0 | 0
0 | 0 | 0 | 0
0 | 0 | 0 | 0
0 | 0 | 0 | 0
0 | 0 | 0 | 0
0 | 0 | 0 | 0
0 | 0 | 0 | 0
0 | 0 | 0 | 0
0 | 0 | 0 | 0
0 | 0 | 0 | 0
0 | 0 | 0 | 0
0 | 0 | 0 | 0
0 | 0 | 0 | 0
0 | 0 | 0 | 0
0 | 0 | 0 | 0
0 | 0 | 0 | 0
0 | 0 | 0 | 0
0 | 0 | 0 | 0
0 | 0 | 0 | 0
0 | 0 | 0 | 0
0 | 0 | 0 | 0
0 | 0 | 0 | 0
0 | 0 | 0 | 0
0 | 0 | 0 | 0
0 | 0 | 0 | 0
0 | 0 | 0 | 0
0 | 0 | 0 | 0
0 | 0 | 0 | 0
#REF! | #REF! | #REF! | #REF!

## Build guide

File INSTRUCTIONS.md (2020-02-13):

# Arribada PMP v1.1 - instruction manual

## Description of operation
When the device is turned on and running, it will periodically enable and disable 5V power supply for Raspberry Pi module.

After enabling the 5V power supply, Raspberry Pi module will turn on, take a picture with Raspberry Pi camera, save it to USB flash drive and then shut itself down. With shutdown Raspberry Pi also signals the main board that it can now disable the 5V supply.

Main board will wait specified amount of time before again turning on the Raspberry Pi which will repeat the cycle.

## Turning on the device
1. Insert batteries into the device. Beware of the correct battery polarity; follow the markings on plastic battery holders.
2. To start the device, click the `battery activate` button in the corner of the board. You will be greeted with the IRNAS logo and Arribada PMP text, which will appear on the OLED display.
3. After the initial boot message on the OLED screen the device should be working normally.

## Checking captured pictures and setting environment variables
To access the captured pictures and to change the settings, user will have to remove the USB flash drive, which is connected to the Raspberry Pi. Two storage places are interesting for the end user, the `camera` directory and the `environment` file.

Captured pictures can be accessed in the `camera` directory. The pictures are named like this: `snapshot-{year}-{month}-{day}--{hour}-{minute}-{second}--{light}-(voltage)-(temperature).jpg`. Light parameter corresponds to light level detected by sensor when taking the photo.

System can be configured by changing the environment variables in the `environment` file, located in the main directory. File can be opened and modified with a text editor, e.g. Notepad or Notepad++.

User can set how long will the Raspberry Pi stay turned off before being turned on to make a photo, which defines the time-lapse interval. This can be set by changing the values of `PIRA_SLEEP` and `PIRA_WAKEUP` variables, which take time values in seconds. Both variables should have the same value. For example, if we want the Raspberry Pi to stay off for 5 minutes before turning it on again, we will set the `PIRA_SLEEP` and `PIRA_WAKEUP` variables both to 300:
*	PIRA_SLEEP="300"
*	PIRA_WAKEUP="300"

In normal operating conditions, Raspberry Pi is turned on for about 40 seconds. This means that setting the variables to 300 will set the time-lapse interval to approx. 340 seconds.

⚠️ ATTENTION! Do not change any other variables to avoid disrupting the operation of the device!

## Accessing the device information on OLED display
Some basic information about the device can be seen on the OLED display. User can see the `current time (UTC)`, `number of captured photos` and `time to next wakeup`. The information is displayed by pressing either `Button 1` or `Button 2` on the side of the board for approx. 5 second.

The current time (UTC) is obtained through the GPS. If there has yet been no GPS fix after the device lost and regained power, a reset date that is saved in memory will be shown, which is 1.1.2020, 00:00.

Number of captured photos and time to next wakeup are obtained from the Raspberry Pi just before the end of each cycle. If no cycle has yet been performed after the device lost and regained power, this information will not be available.

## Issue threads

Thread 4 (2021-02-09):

### ISSUE TITLE
Display power consumption

### ISSUE THREAD

**Issue by sakalaka8** [IRNAS/arribada-pmp#4]

**Comment by SloMusti** [comment]
Please report the power consumption results here

**Comment by sakalaka8** [comment]
![i2c_display_consumption](https://user-images.githubusercontent.com/43861607/66556923-599f4800-eb51-11e9-9451-58fc8df94951.png)
Average power consumption  of I2C display: 5.20 uA 
Display was measured between Vcc line and GND.

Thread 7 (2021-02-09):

### ISSUE TITLE
U13 - BME280 fix layout

### ISSUE THREAD

**Issue by SloMusti** [IRNAS/arribada-pmp#7]
THe BME280 sensor does not have a good footprint, GND pad is missing a thermal relief + there must be a mechanical cutout to provide thermal stress relief to the sensor.

**Comment by sakalaka8** [comment]
![slika](https://user-images.githubusercontent.com/43861607/94649424-ef992900-02f4-11eb-84e0-446cea20113a.png)
The BME280 sensor has fixed issues with GND pad around and mechanical cutout.

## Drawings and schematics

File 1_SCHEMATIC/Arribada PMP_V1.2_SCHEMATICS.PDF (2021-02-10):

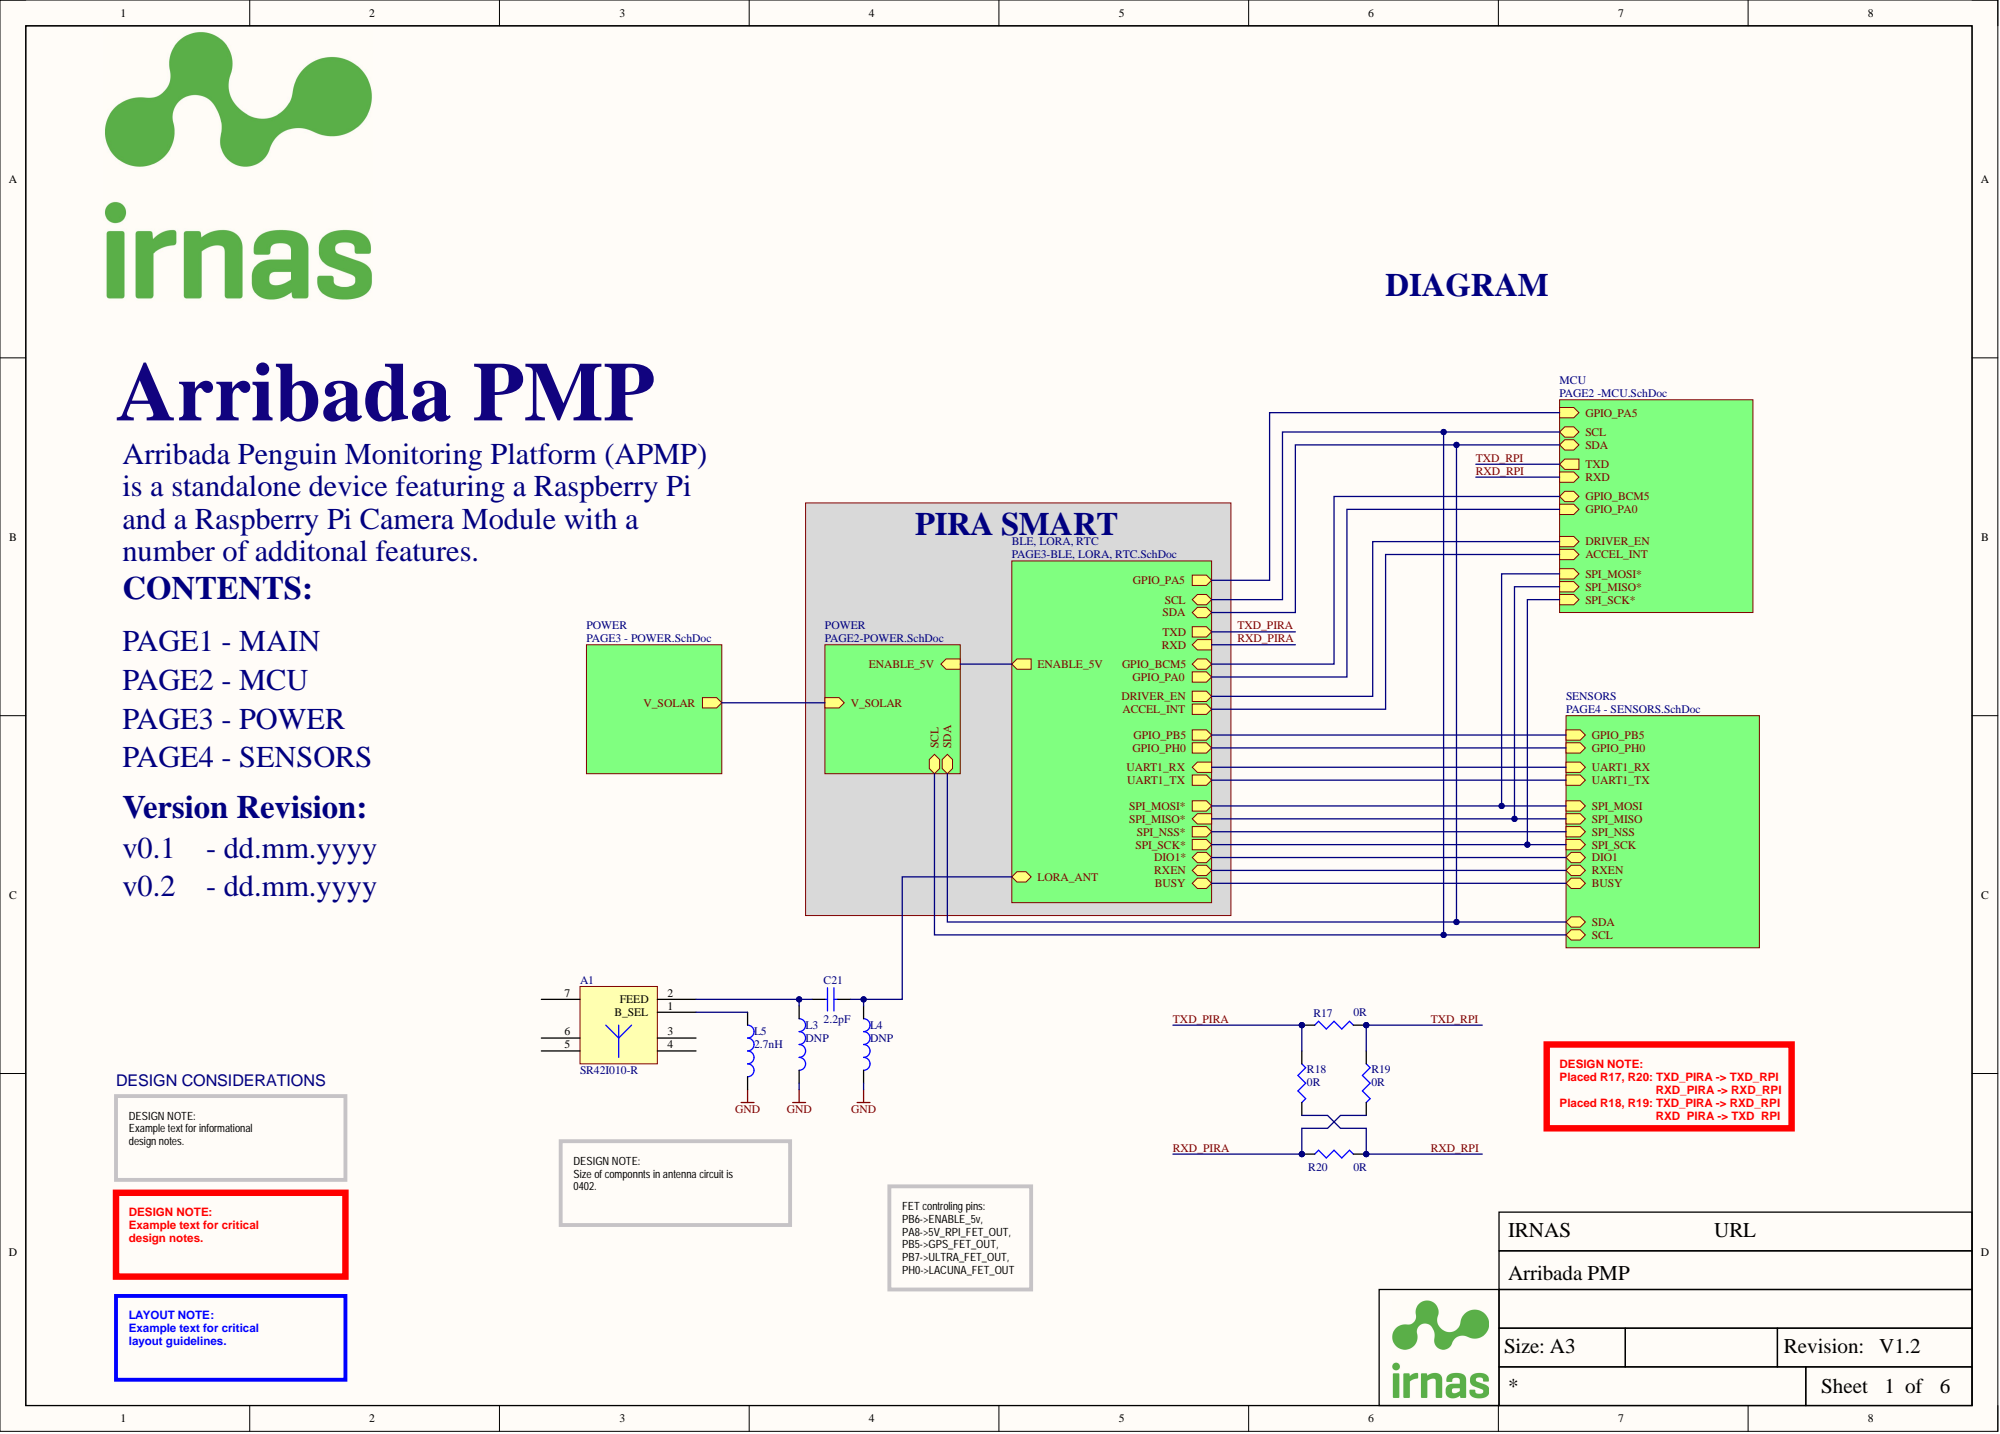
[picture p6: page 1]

Arribada Penguin Monitoring Platform (APMP)
is a standalone device featuring a Raspberry Pi
number of additonal features.
CONTENTS: PAGE1 - MAIN PAGE2 - MCU Version Revision:

TXD_RPI RXD_RPI

T BLE, LORA, RTC PAGE3-BLE, LORA, RTC.SchDoc

DESIGN NOTE:
Example text for informational
design notes.

Size of componnts in antenna circuit is

Example text for critical

LAYOUT NOTE:
layout guidelines.

Size: A3 | | Revision: V1.2

Sheet of

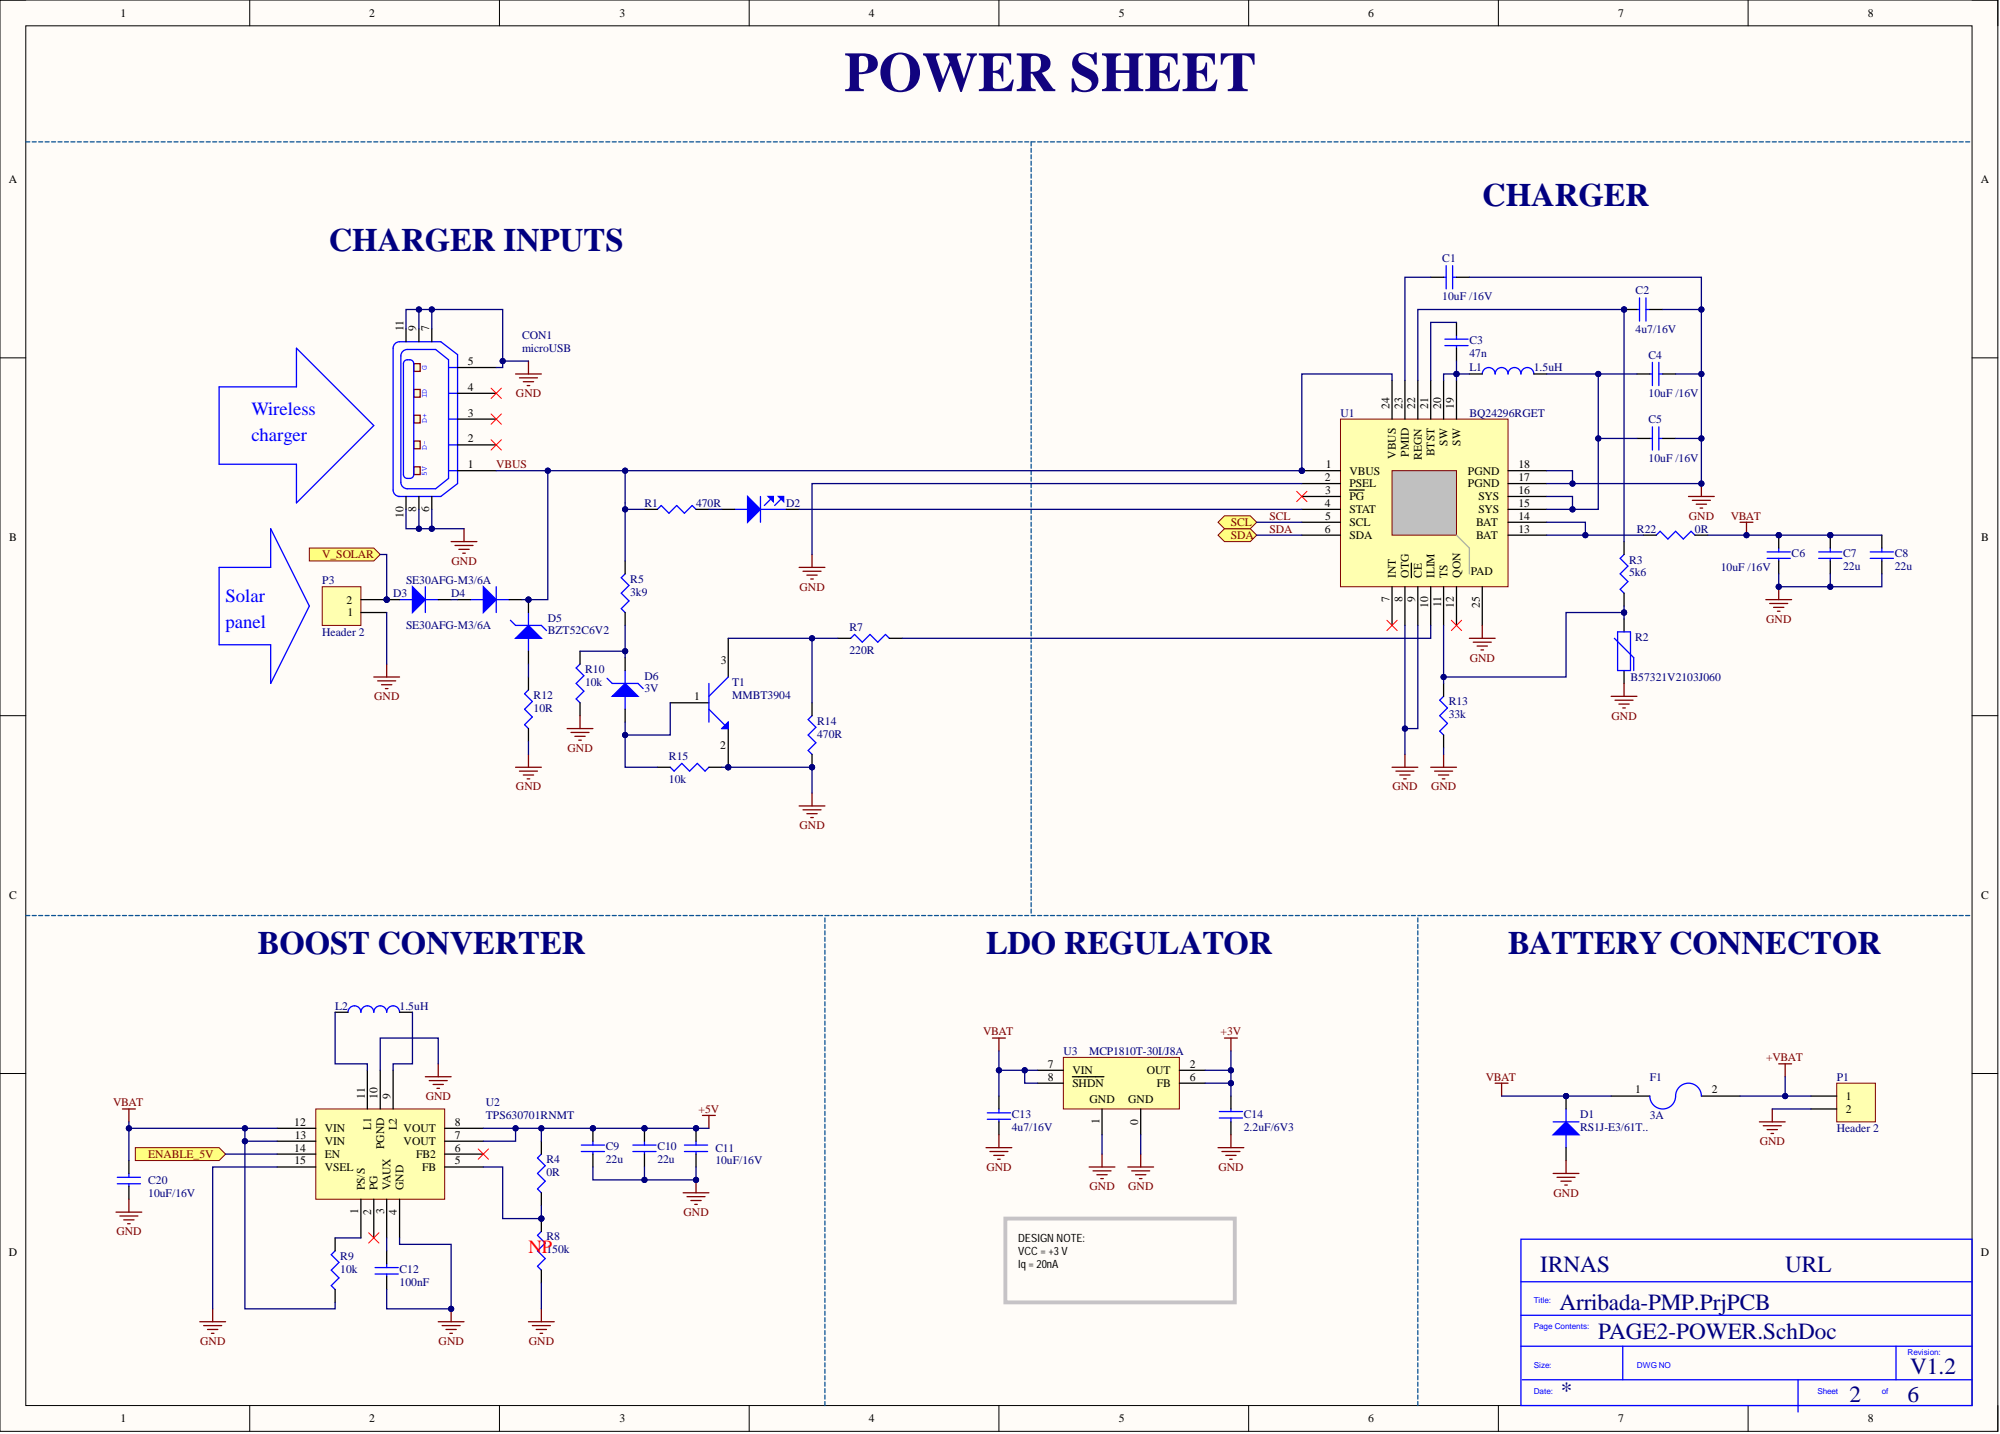
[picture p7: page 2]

SW 19 SW 20 BTST 21 REGN 22 PMID 23 VBUS 24

SCL SCL SDA | SCL 5 SDA 6

VIN 13
EN 14 VSEL 15

Size: | DWG NO | Revision:

Date:

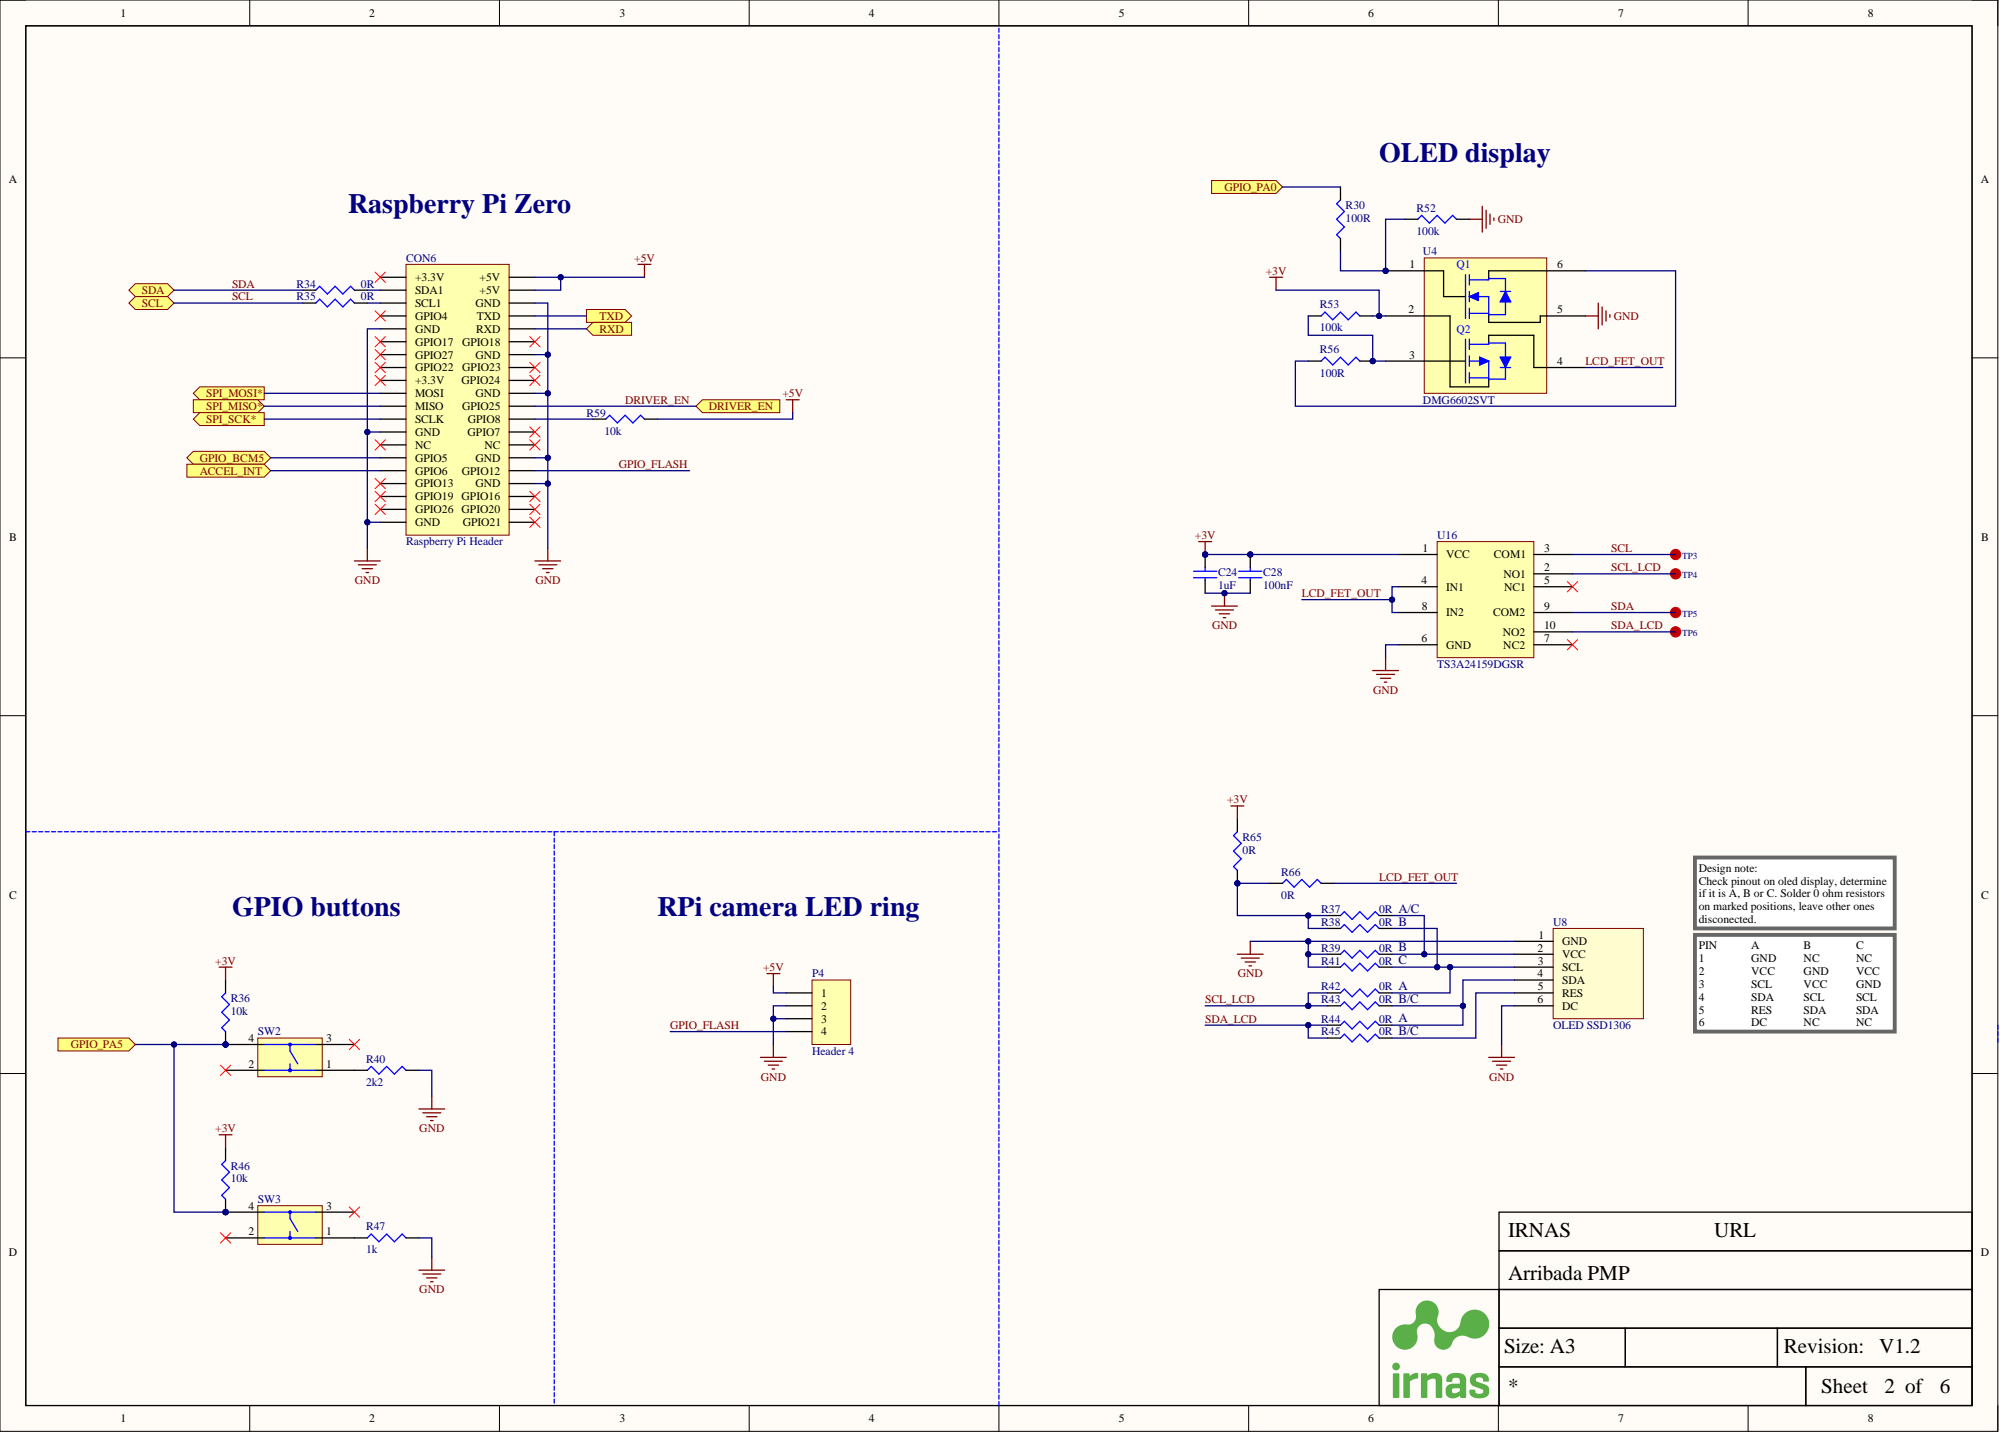
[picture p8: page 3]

Design note:
Check pinout on oled display, determine
if it is A, B or C. Solder 0 ohm resistors
on marked positions, leave other ones
disconected.

RPi camera LED ring

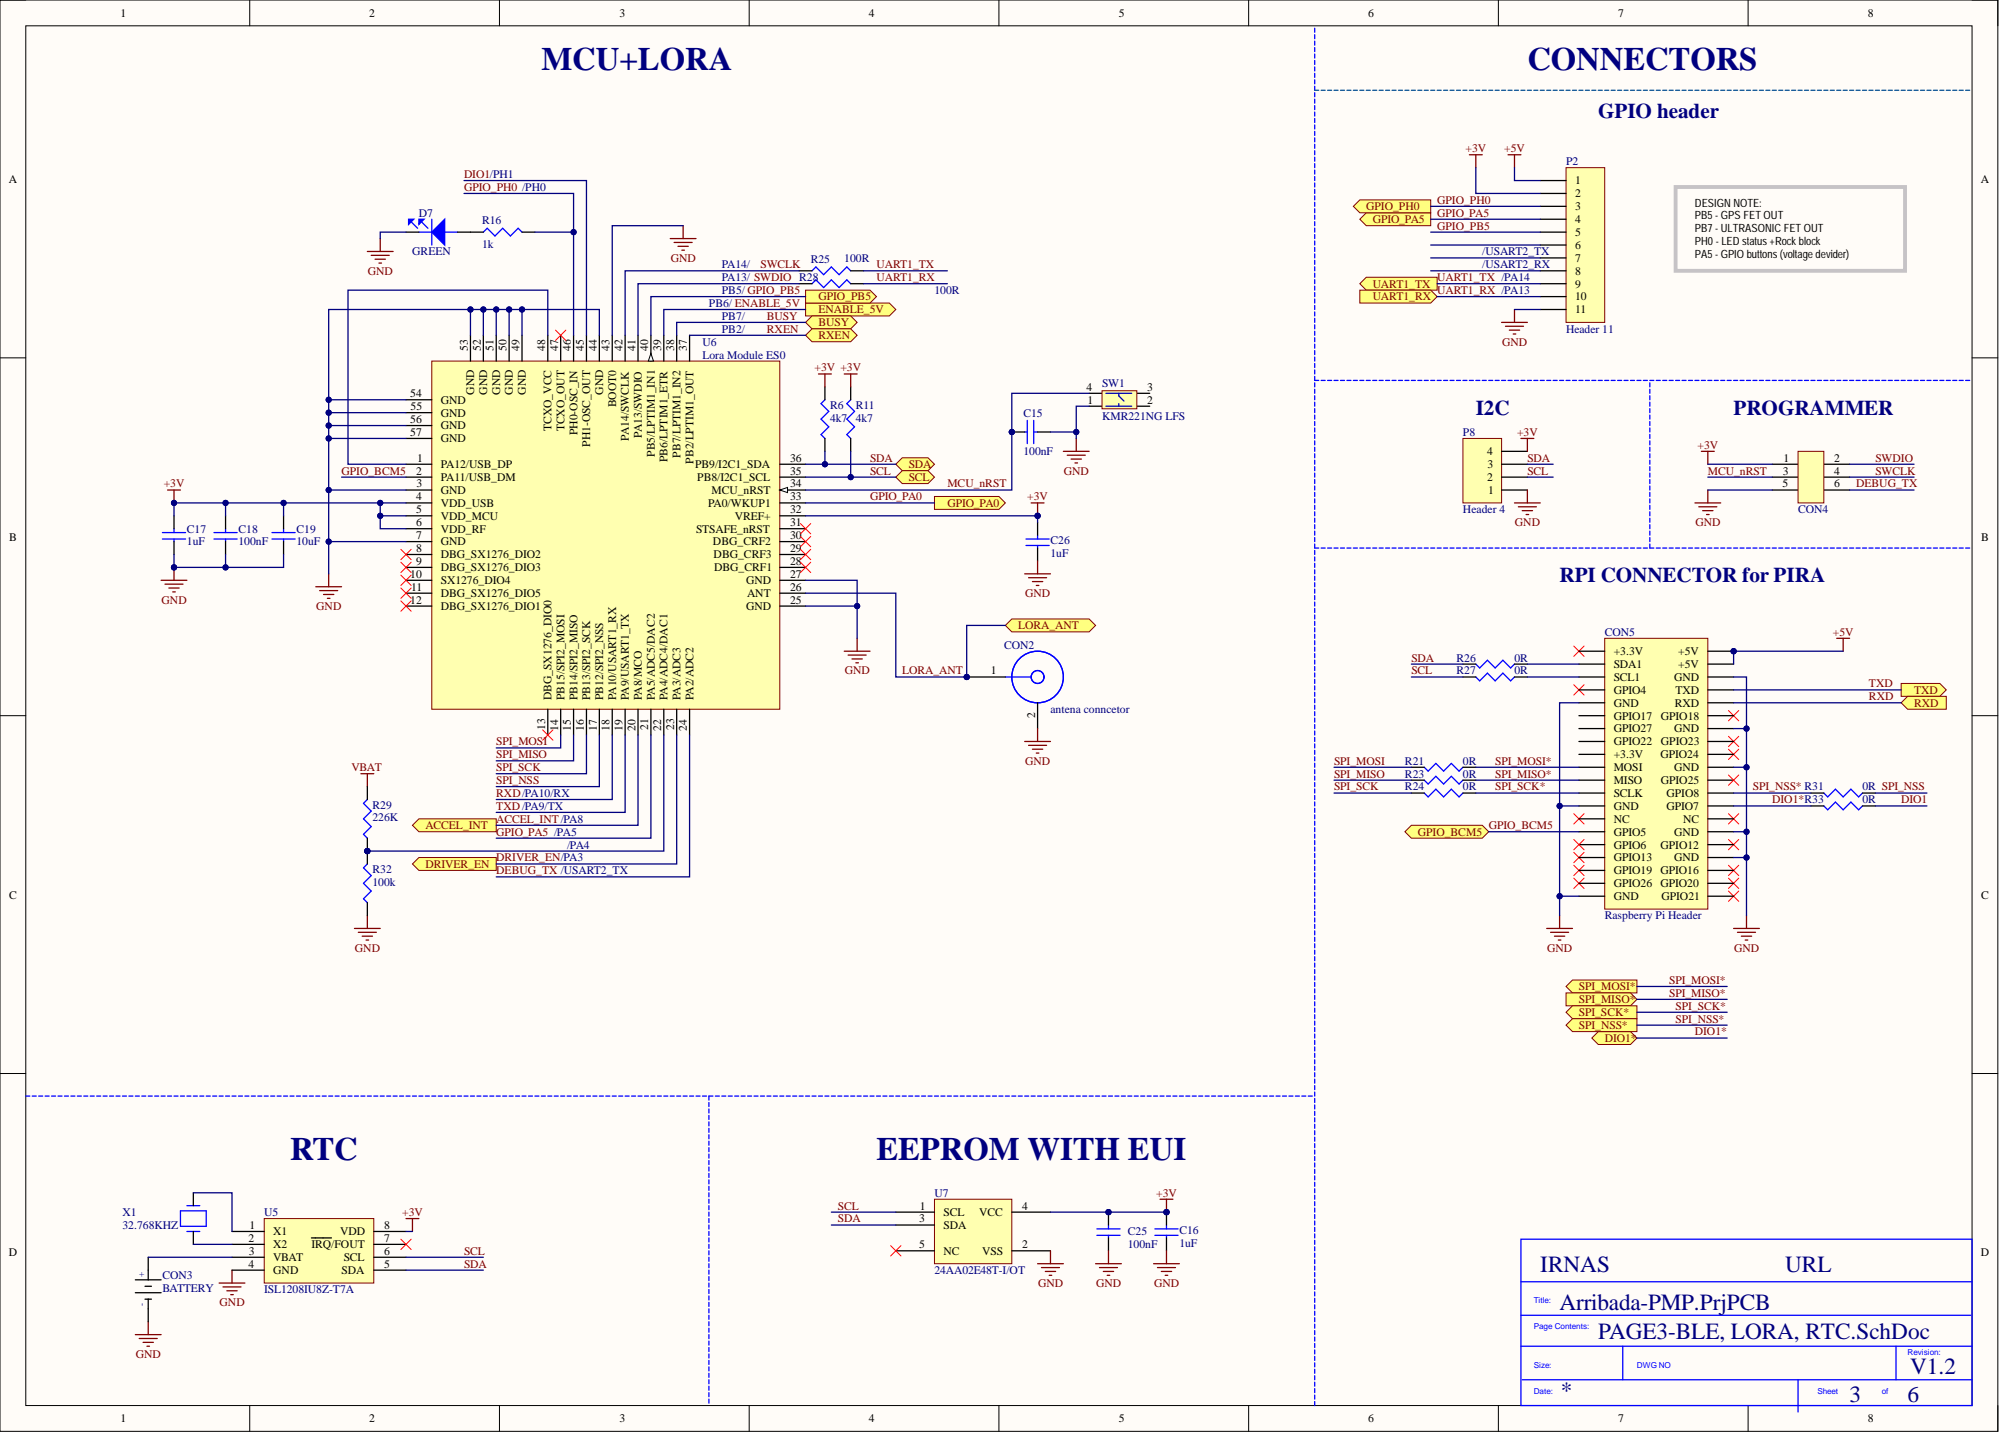
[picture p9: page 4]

DESIGN NOTE:
PB5 - GPS FET OUT
PB7 - ULTRASONIC FET OUT
PH0 - LED status +Rock block
PA5 - GPIO buttons (voltage devider)

1k GREEN

PB6/ ENABLE_5V
PB7/ BUSY

GND 50 GND 51 GND 52 GND 53

GND 55

GND 57

MCU_nRST

VDD_USB 4
VDD_MCU 5
VDD_RF 6

RPI CONNECTOR for PIRA

Arribada-PMP.PrjPCB
PAGE3-BLE, LORA, RTC.SchDoc

Size: | DWG NO | Revision:

Date:

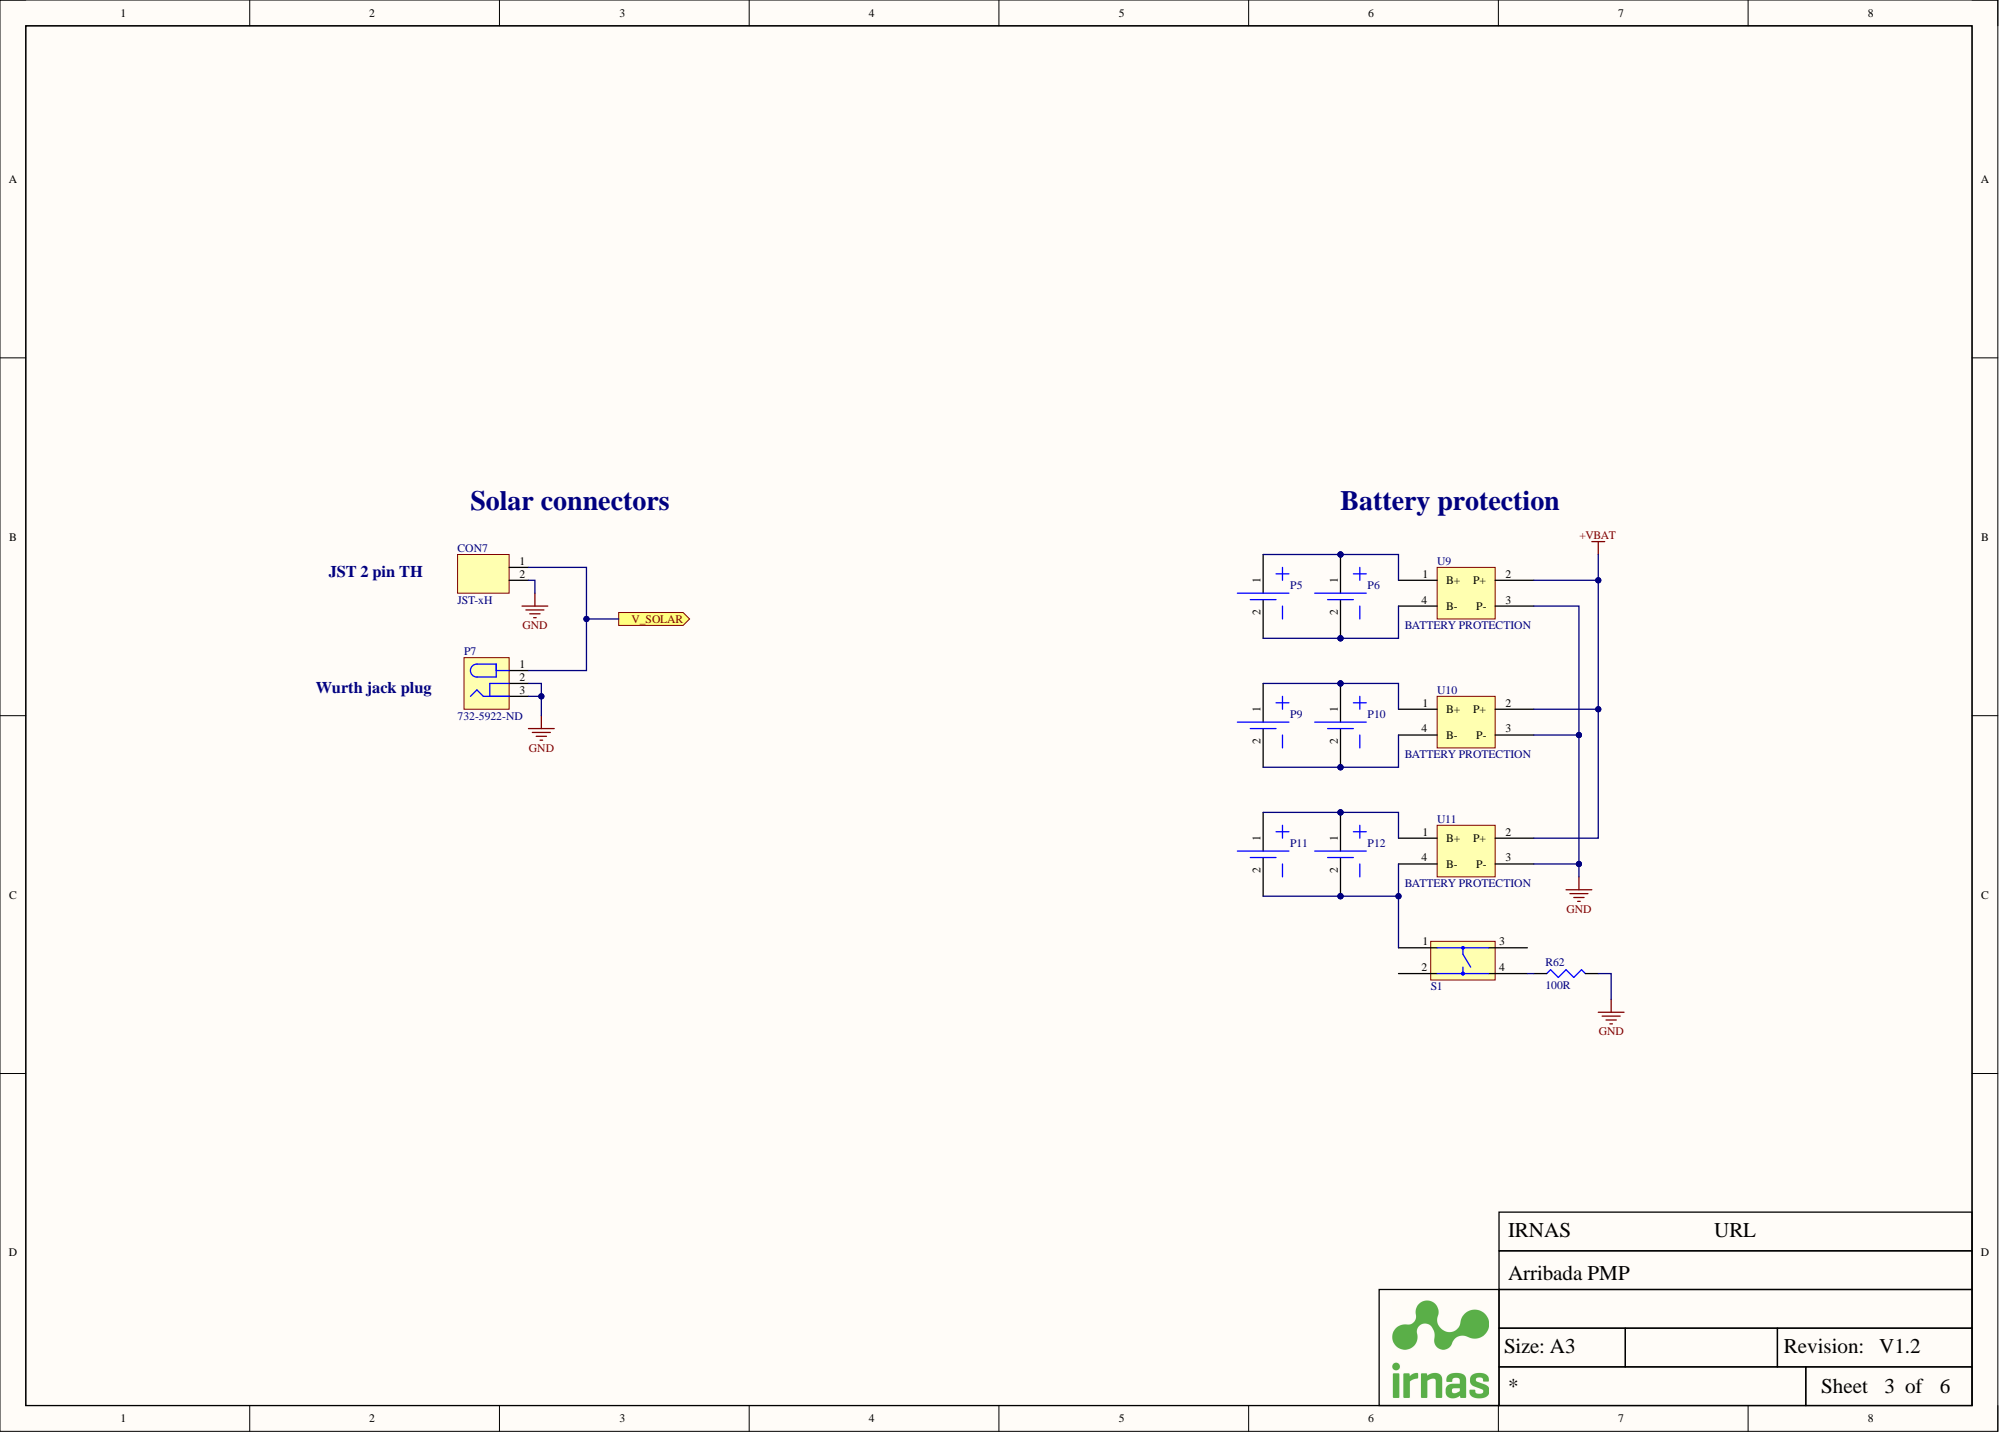
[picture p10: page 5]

JST 2 pin TH Wurth jack plug

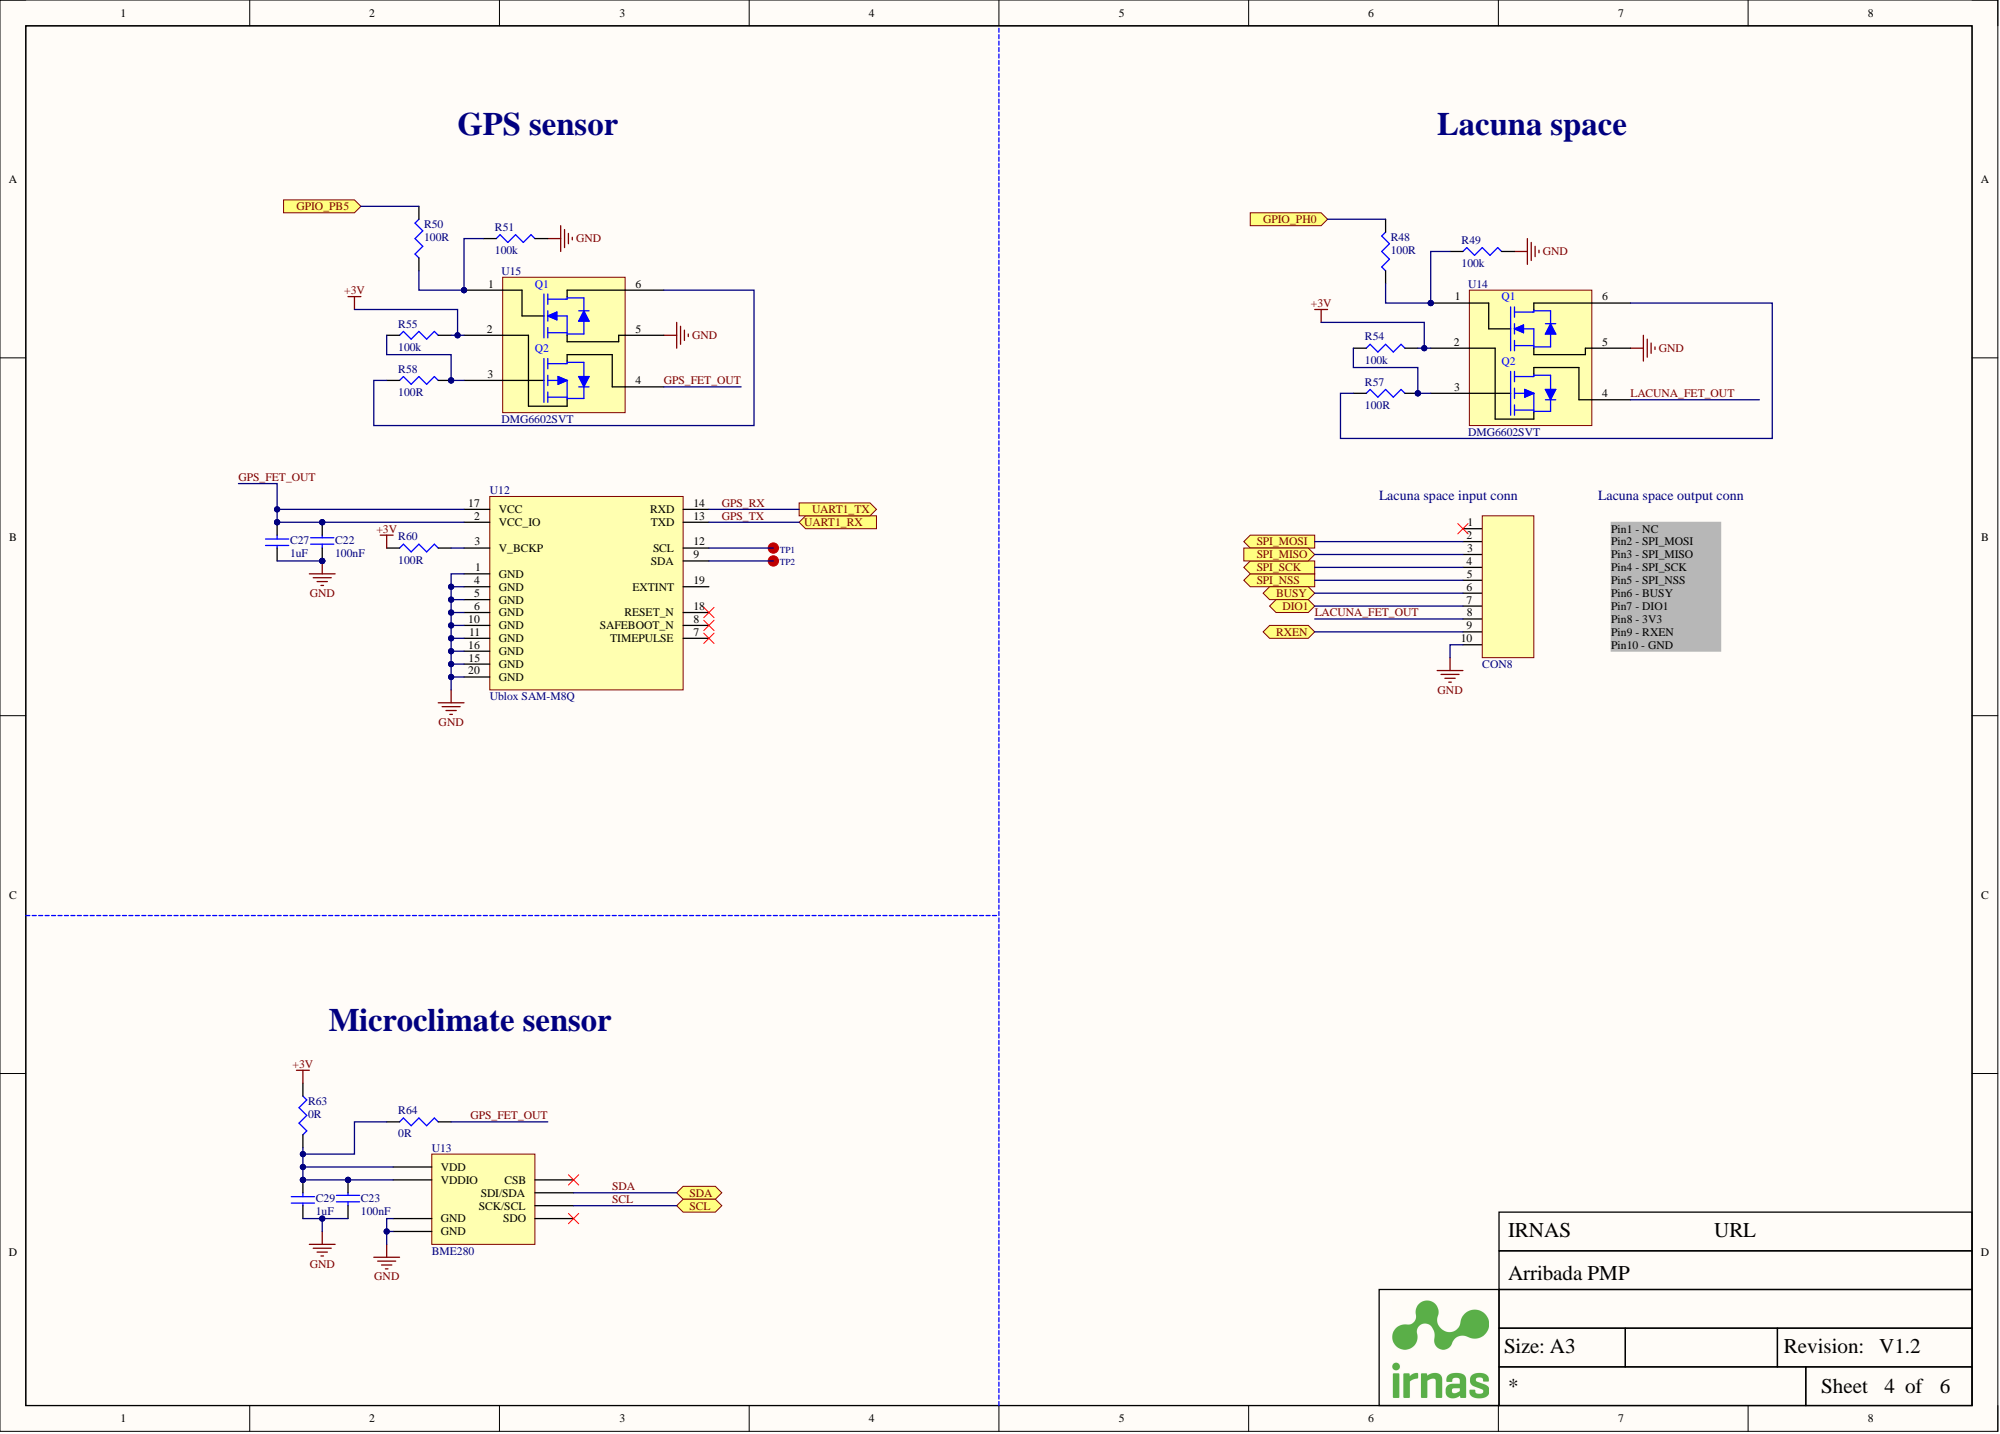
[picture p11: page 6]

GND 15 GND 16

GND 20

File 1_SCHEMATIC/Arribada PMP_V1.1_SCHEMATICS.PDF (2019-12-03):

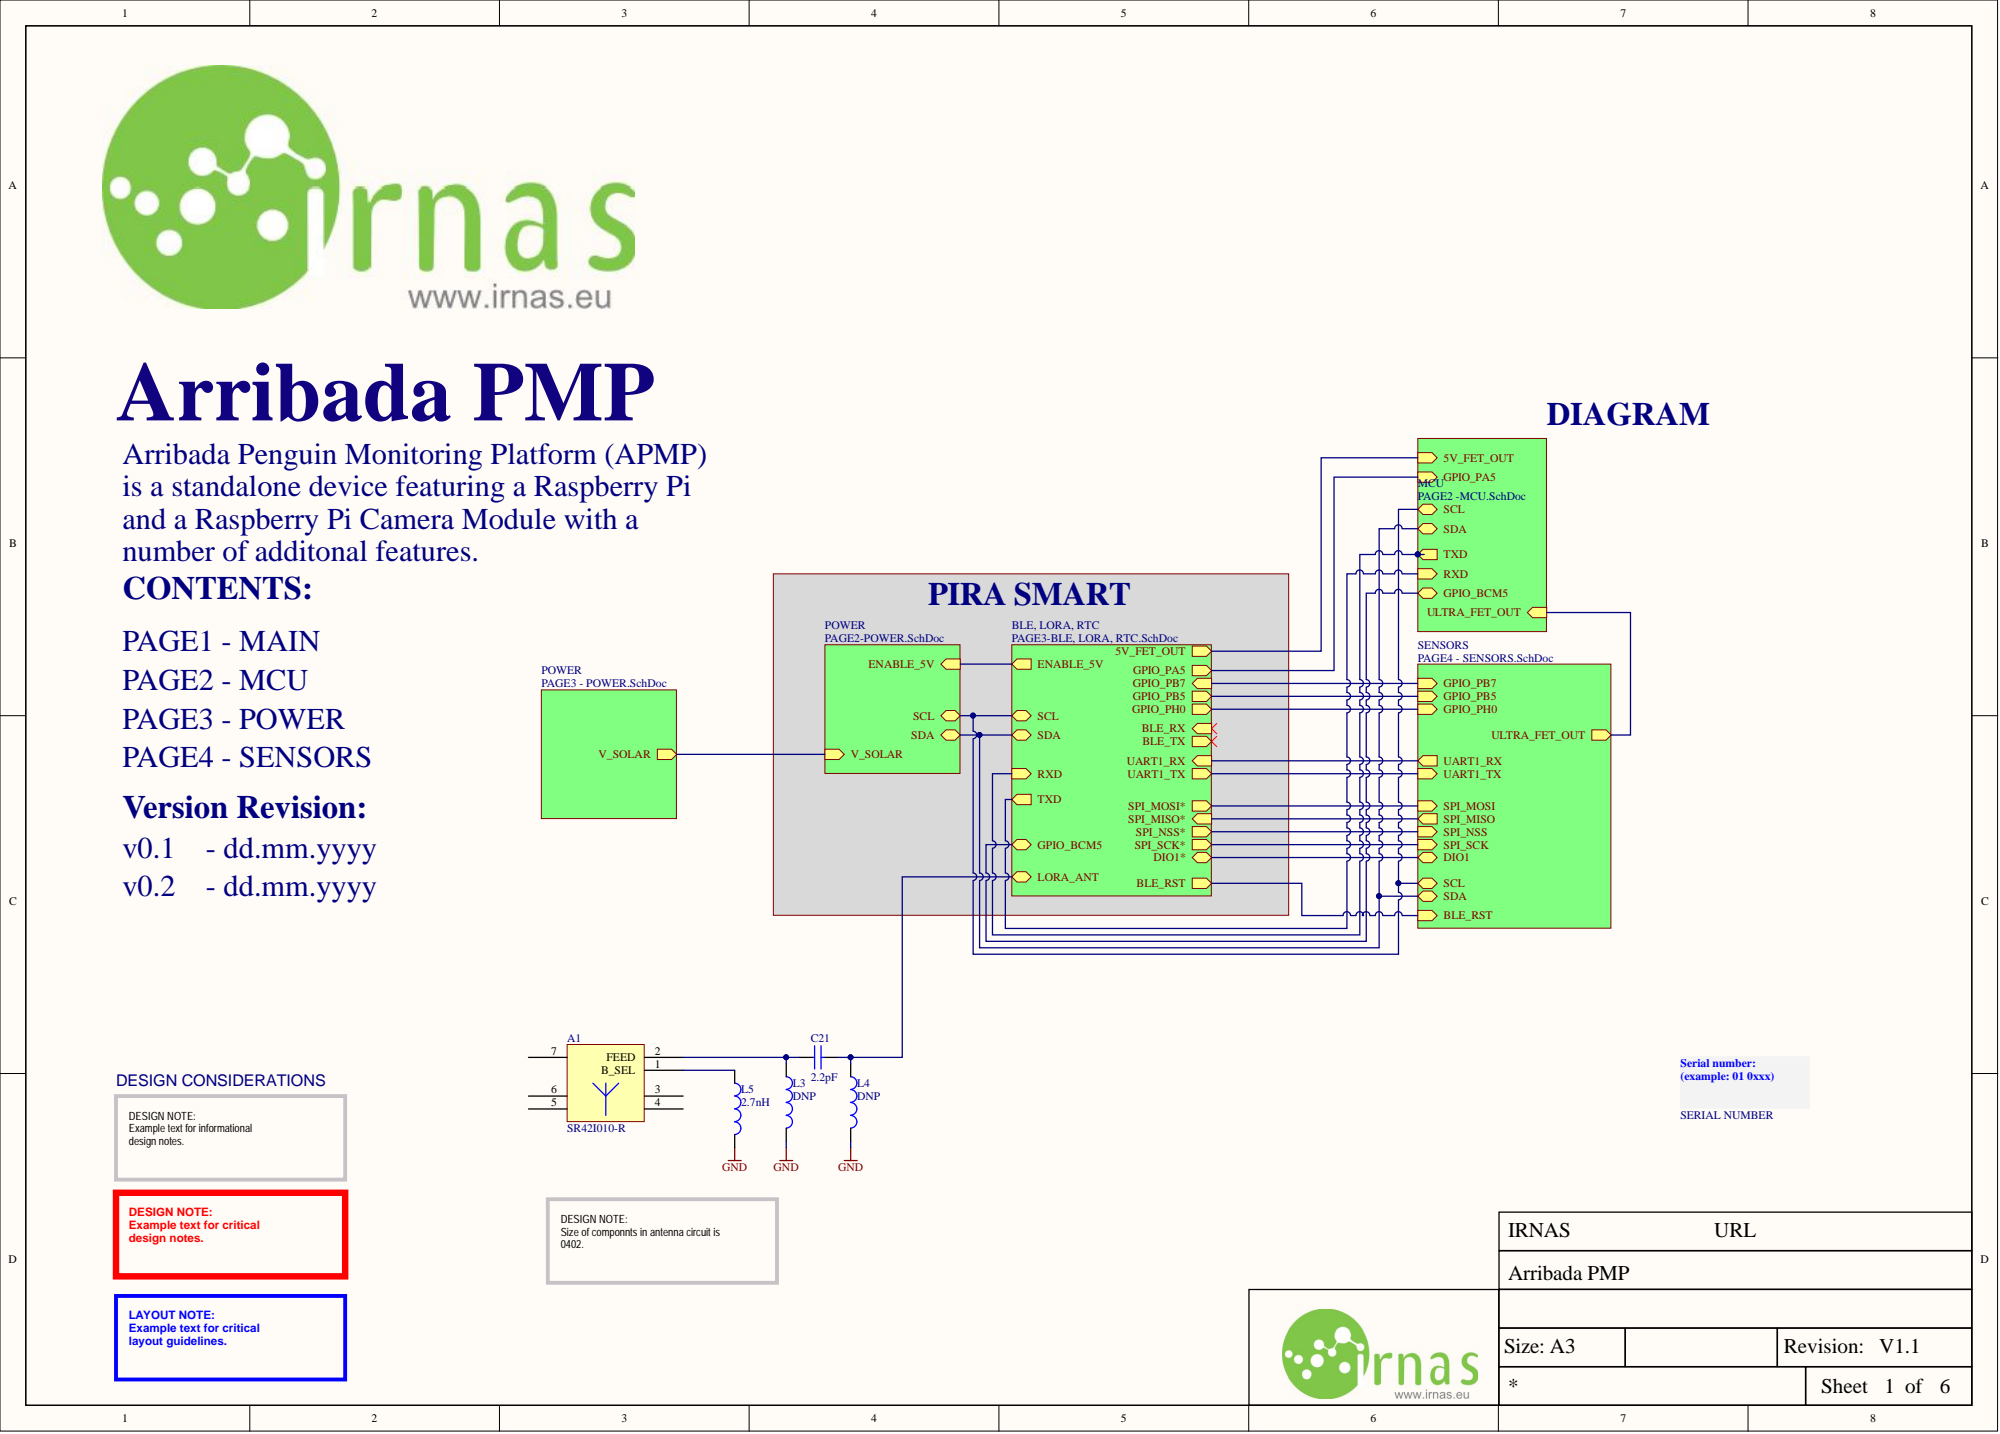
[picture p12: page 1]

Arribada Penguin Monitoring Platform (APMP)
is a standalone device featuring a Raspberry Pi
and a Raspberry Pi Camera Module with a
number of additonal features.
CONTENTS: PAGE1 - MAIN PAGE2 - MCU Version Revision:

BLE, LORA, RTC PAGE3-BLE, LORA, RTC.SchDoc

LORA_ANT

BLE_RST

DESIGN NOTE:
Example text for informational
design notes.

Example text for critical

Size of componnts in antenna circuit is

LAYOUT NOTE:
layout guidelines.

Size: A3 | | Revision: V1.1

Sheet of

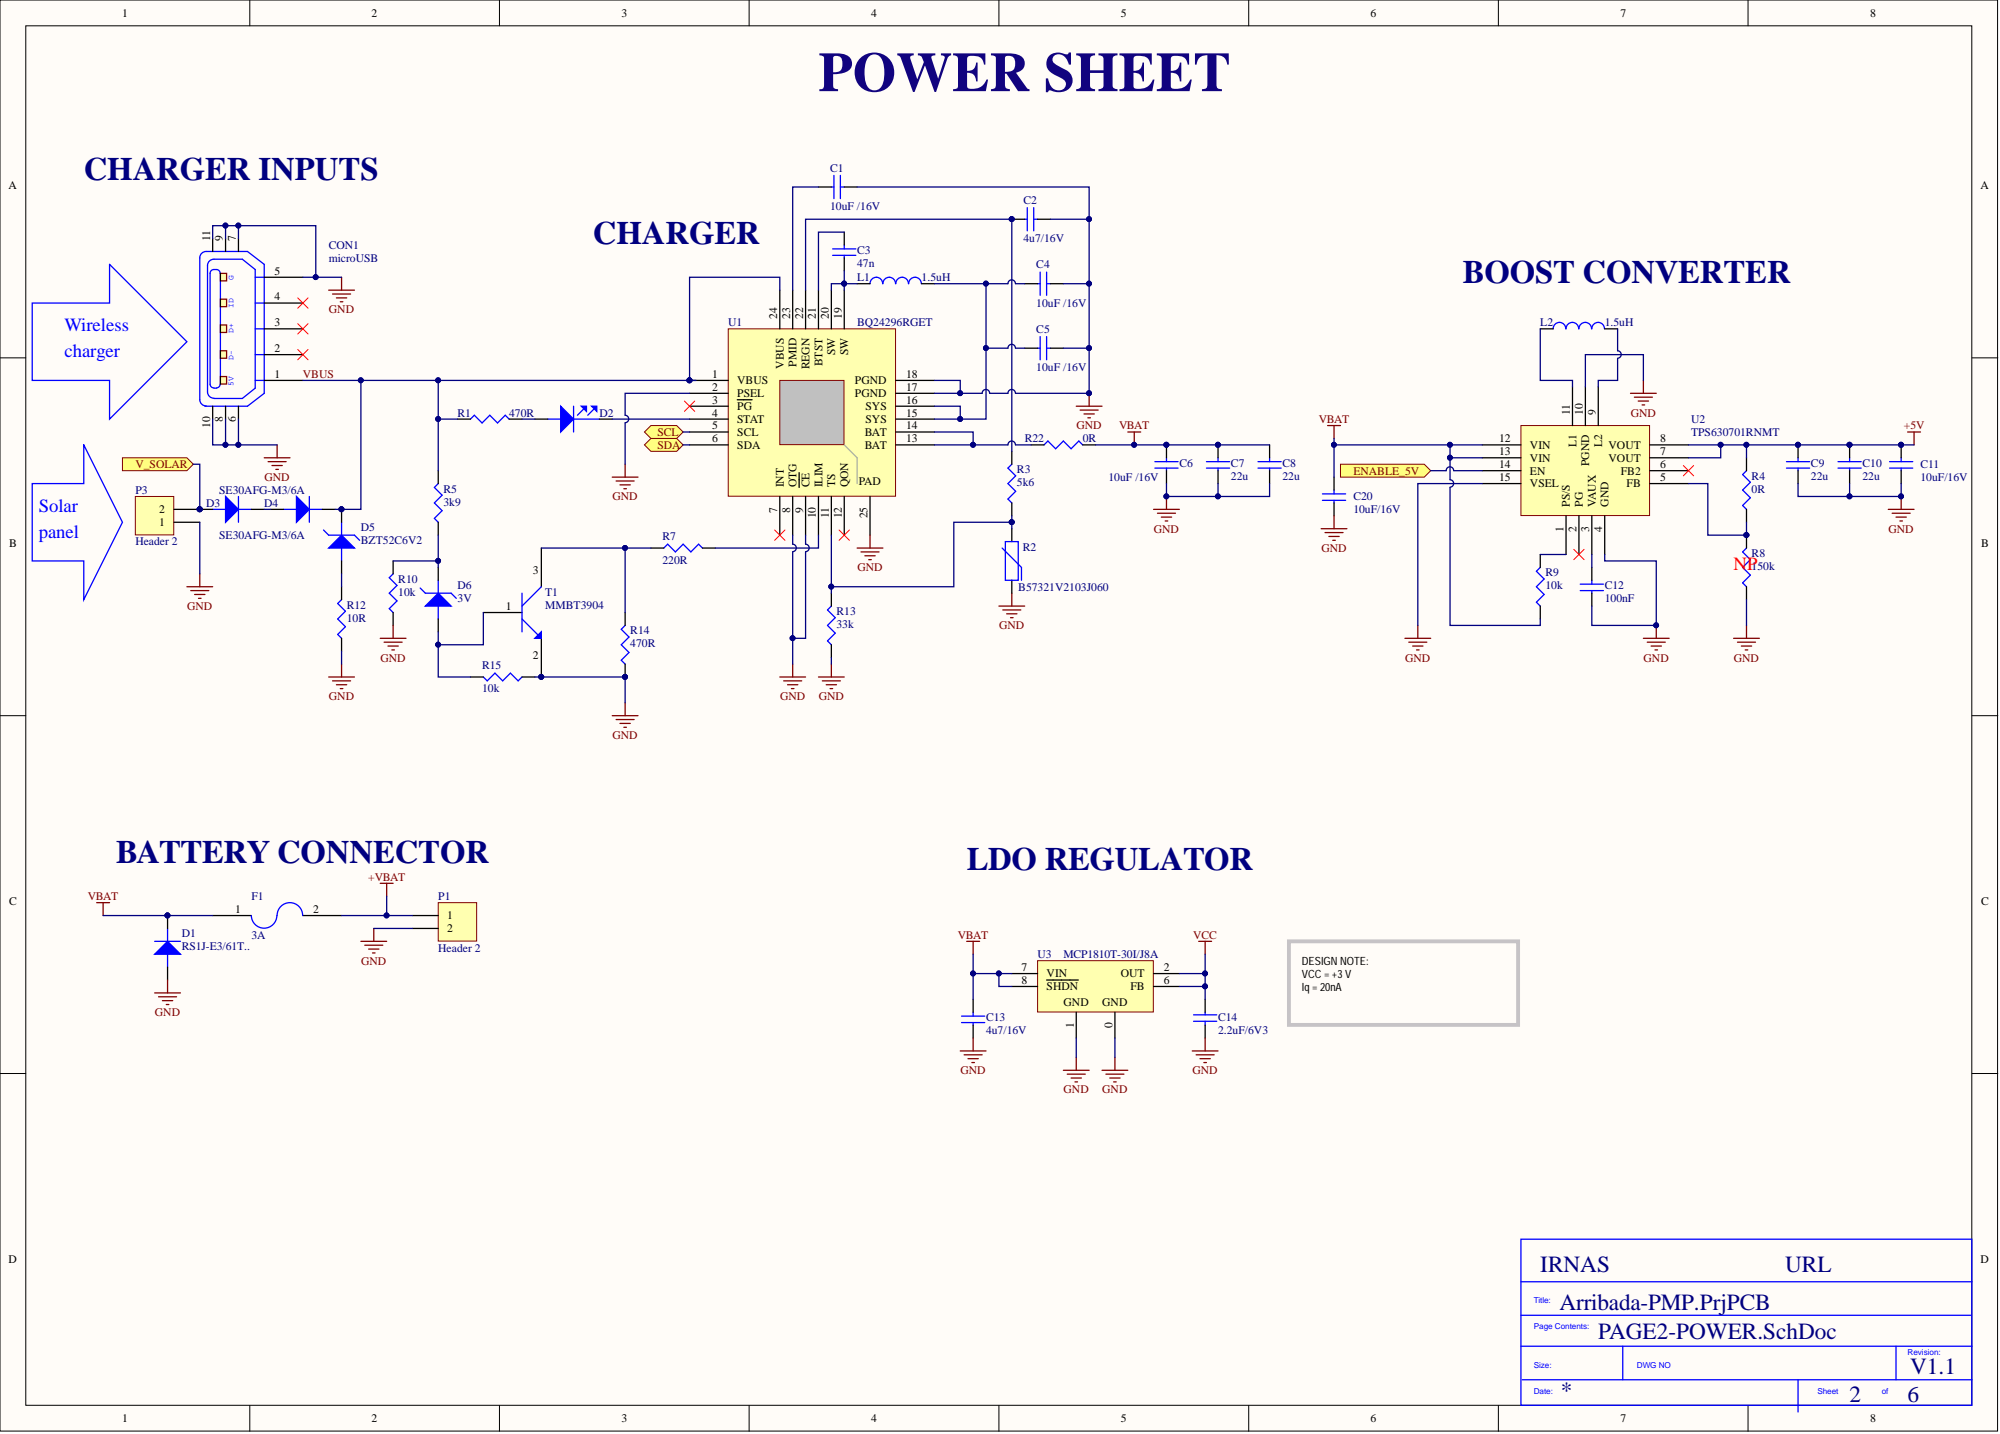
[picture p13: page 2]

SW 19 SW 20 BTST 21 REGN 22 PMID 23 VBUS 24

VBUS 1

Size: | DWG NO | Revision:

Date:

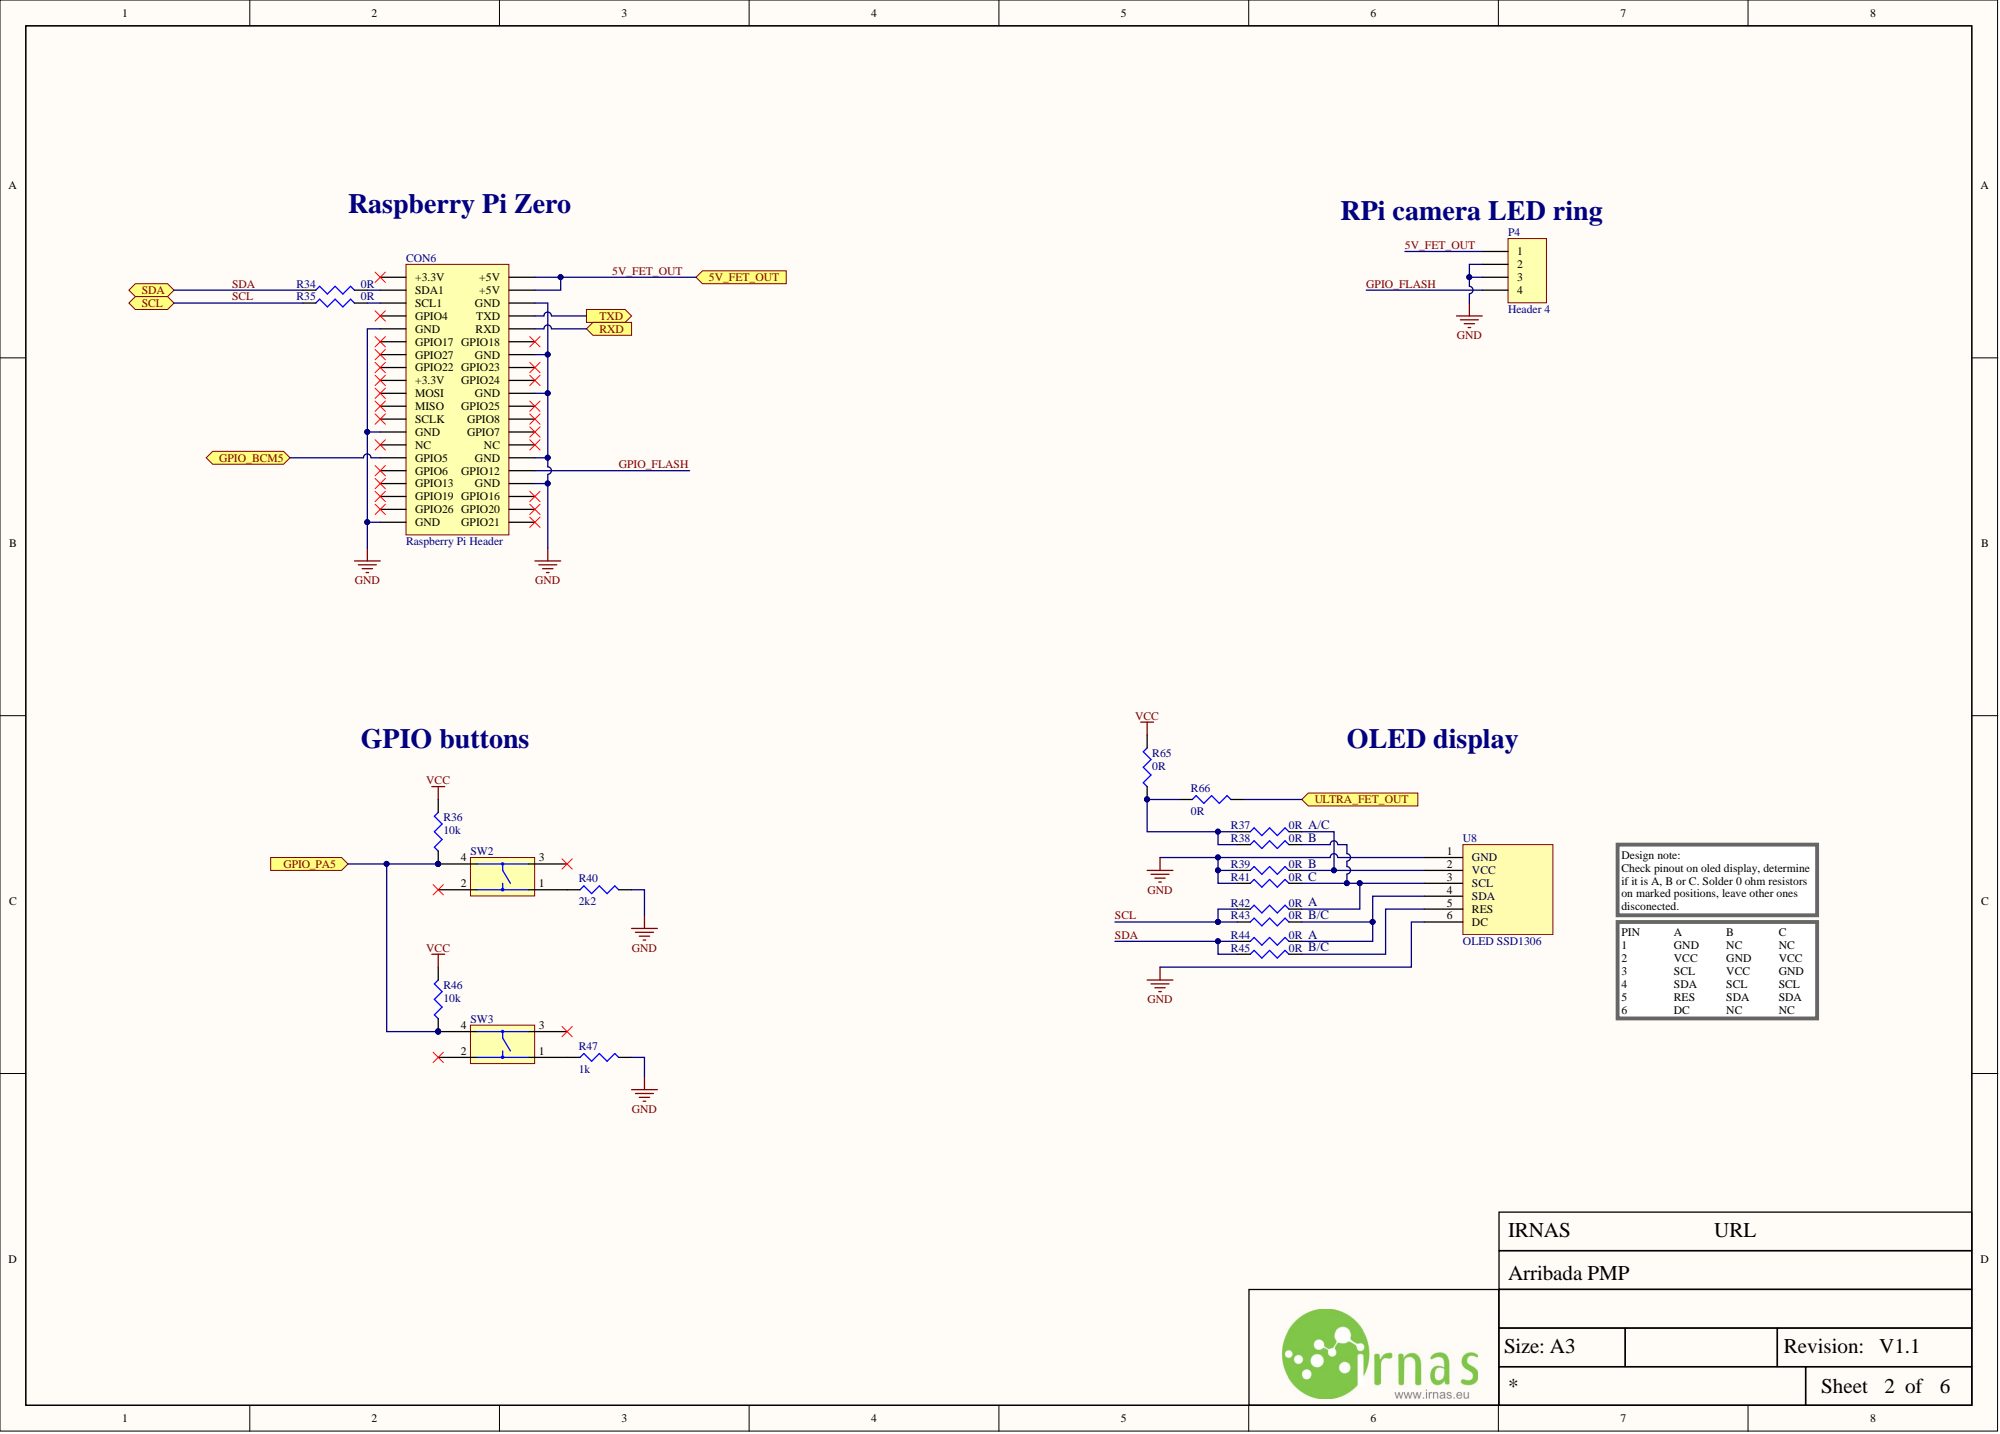
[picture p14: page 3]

RPi camera LED ring

Design note:
Check pinout on oled display, determine
if it is A, B or C. Solder 0 ohm resistors
on marked positions, leave other ones
disconected.

VCC 2 SCL 3 SDA 4

RES 5 DC 6

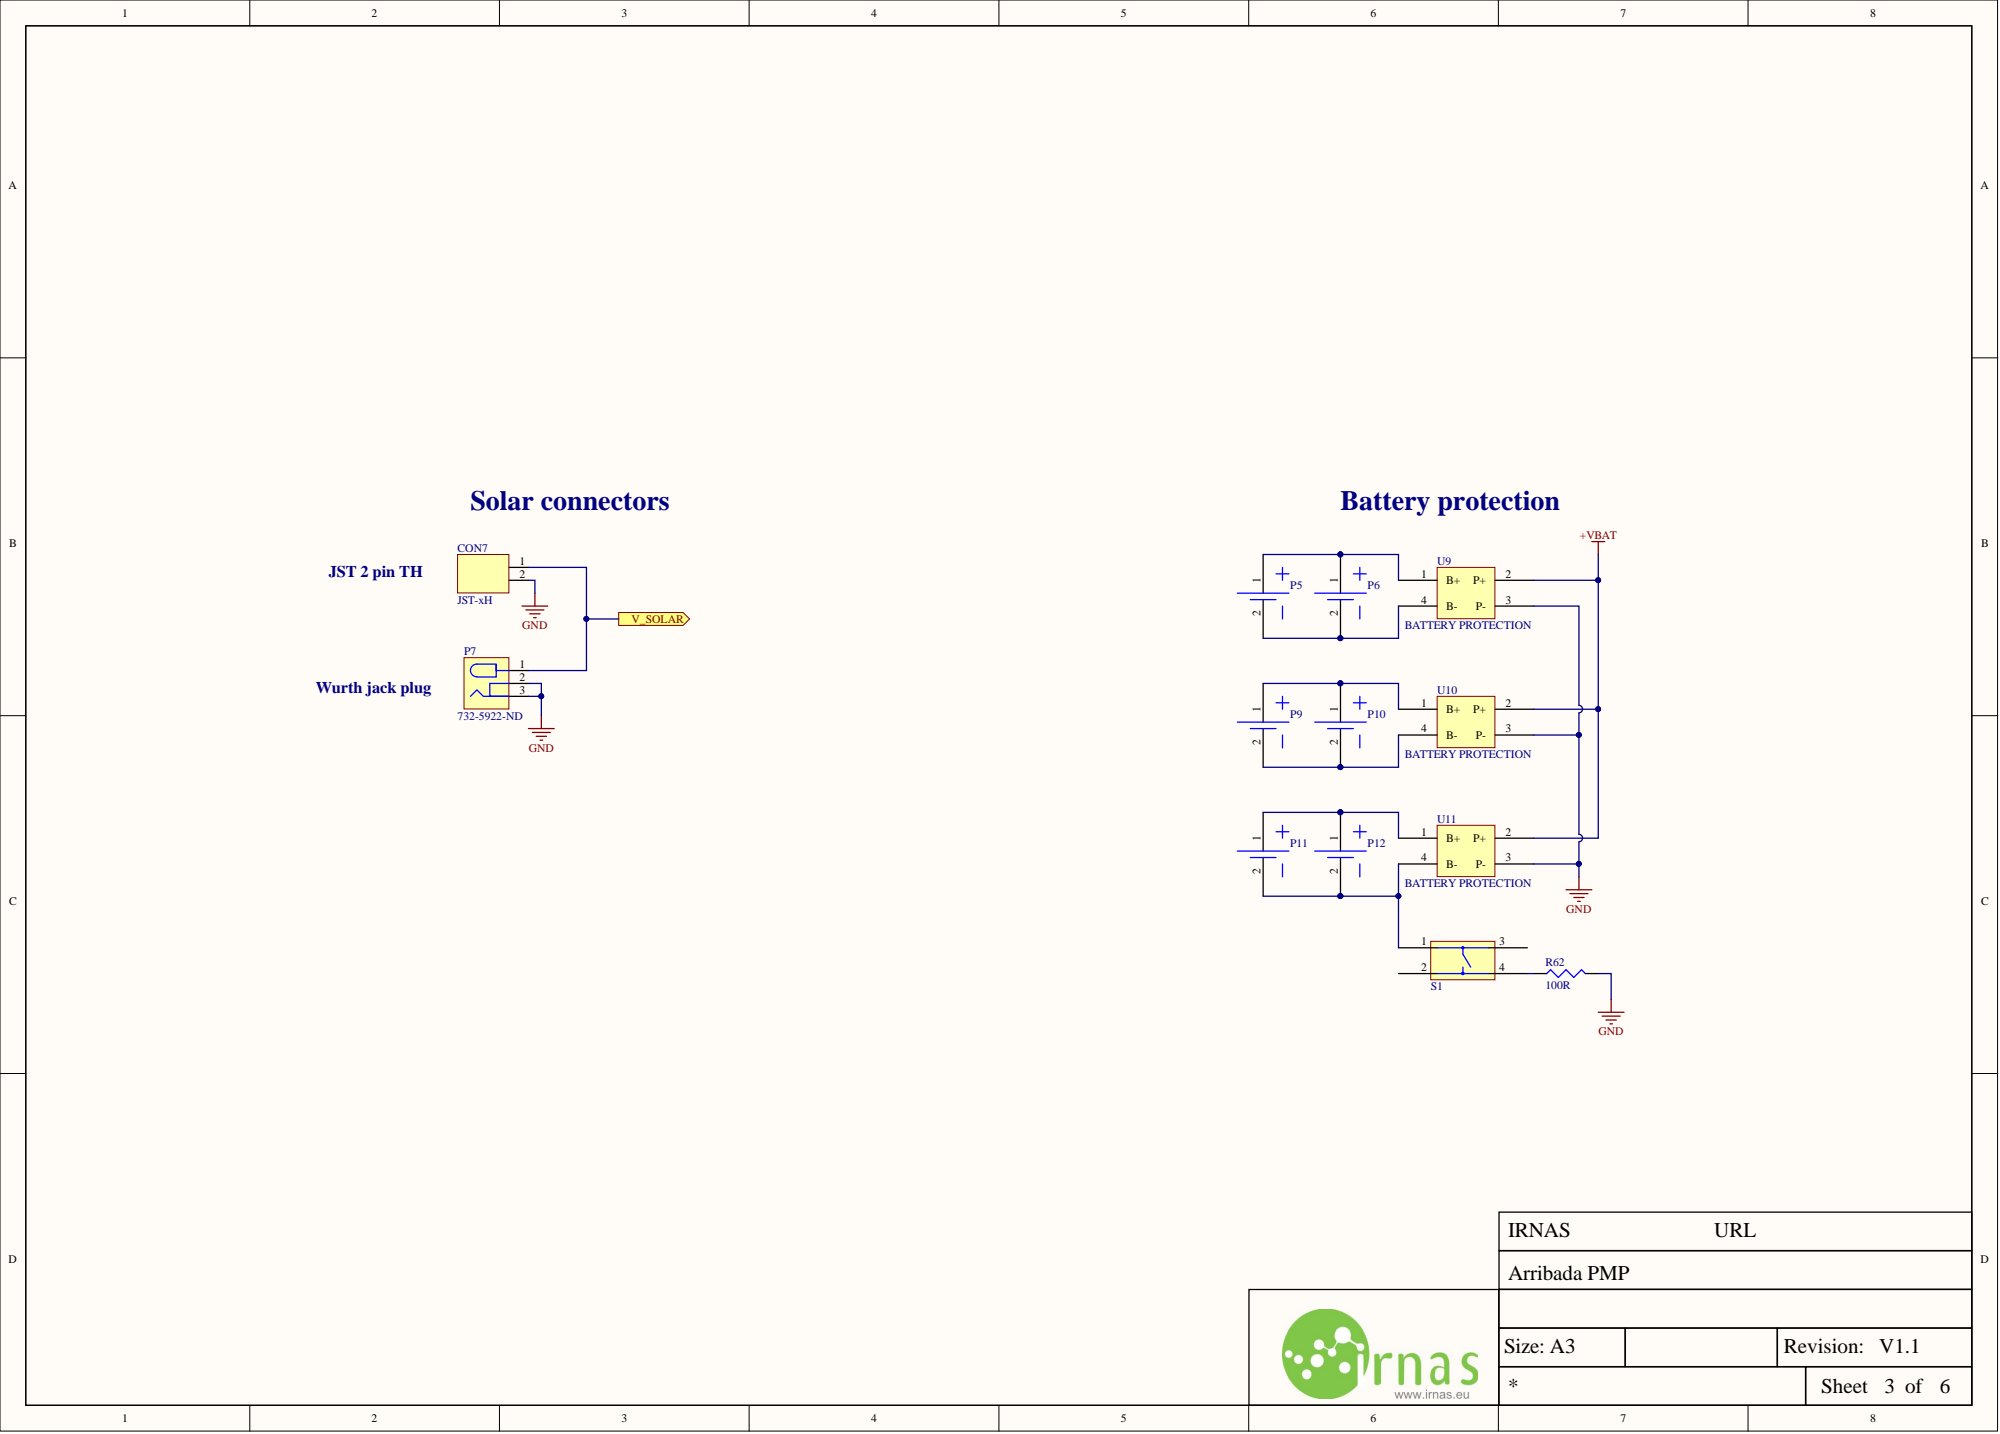
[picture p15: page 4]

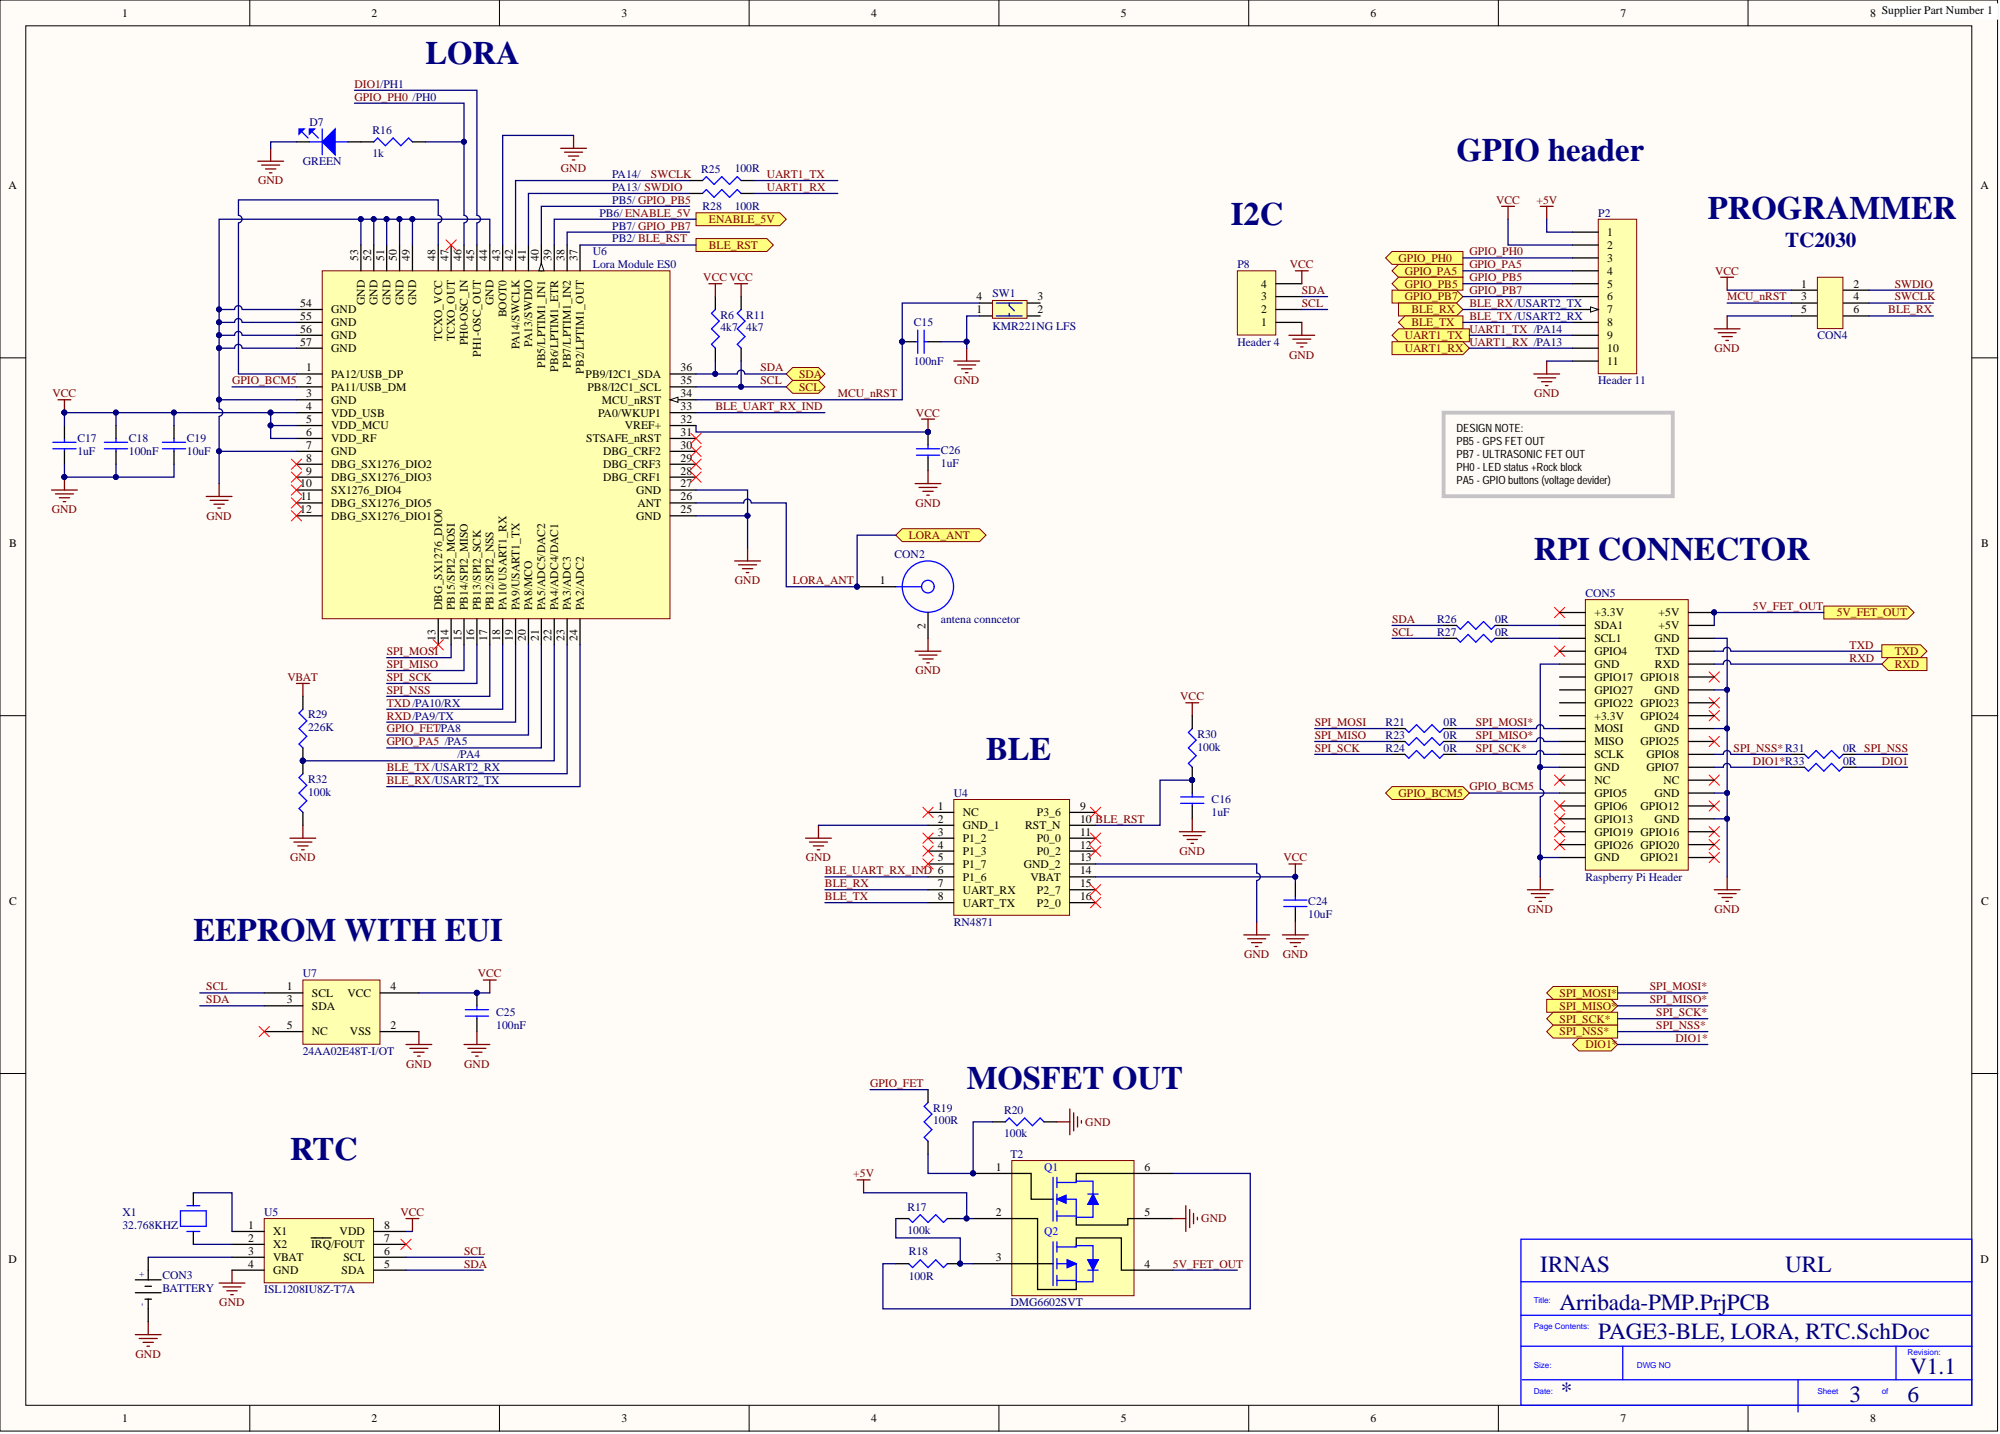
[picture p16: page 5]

GND 50 GND 51 GND 52 GND 53

GND 55
GND 56
GND 57

PA12/USB_DP 1

MCU_nRST

VDD_USB 4

VDD_RF 6

DESIGN NOTE:
PB5 - GPS FET OUT
PB7 - ULTRASONIC FET OUT
PH0 - LED status +Rock block
PA5 - GPIO buttons (voltage devider)

Arribada-PMP.PrjPCB
PAGE3-BLE, LORA, RTC.SchDoc

Size: | DWG NO | Revision:

Date:

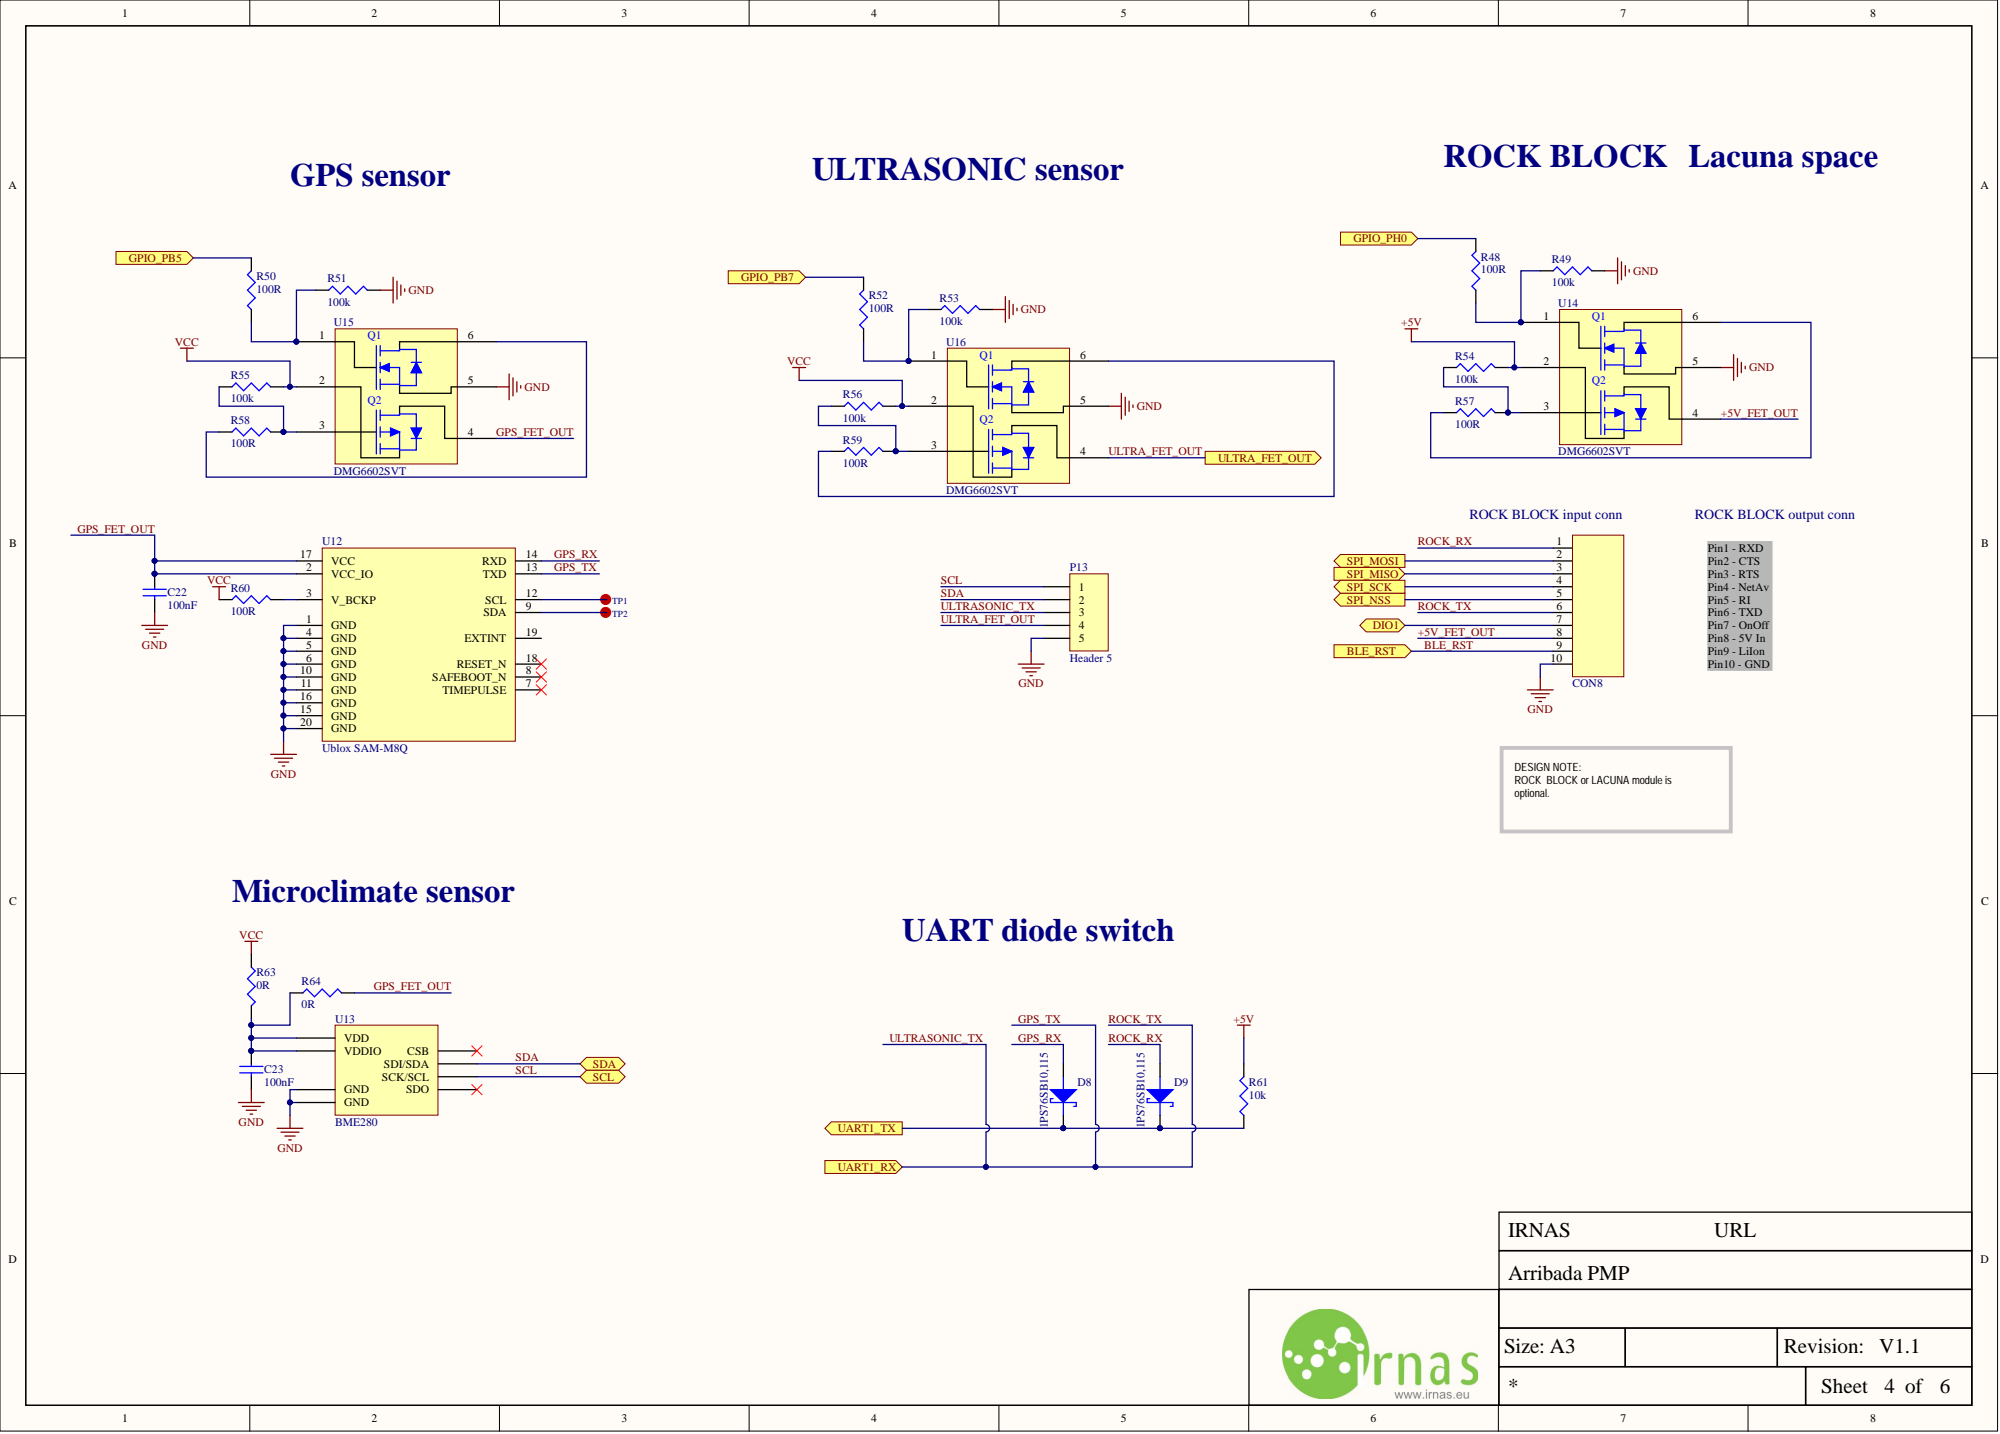
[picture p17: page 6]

GND 15 GND 16

GND 20

DESIGN NOTE:
ROCK BLOCK or LACUNA module is
optional.











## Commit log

2019-10-05 Upload documents
    [Arribada PMP_V0.1_ACTIVE_BOM.xlsx, Arribada-PMP.PrjPCB, PAGE1 - MAIN.SchDoc, PAGE2 -MCU.SchDoc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]
2019-11-28 Release v1.0
    [Arribada PMP_V0.1_ACTIVE_BOM.xlsx, Arribada-PMP.PrjPCB, PAGE1 - MAIN.SchDoc, PAGE2 -MCU.SchDoc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]
2019-12-03 Update documenation
    [Arribada PMP_V1.1_ACTIVE_BOM.xlsx]
2021-02-09 Release V1.2
    In this release are minimal changes that were required to run the applications.
    [Arribada PMP_V0.1_ACTIVE_BOM.xlsx, Arribada PMP_V1.2.DRL, Arribada PMP_V1.2.GBL, Arribada PMP_V1.2.GBO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]
